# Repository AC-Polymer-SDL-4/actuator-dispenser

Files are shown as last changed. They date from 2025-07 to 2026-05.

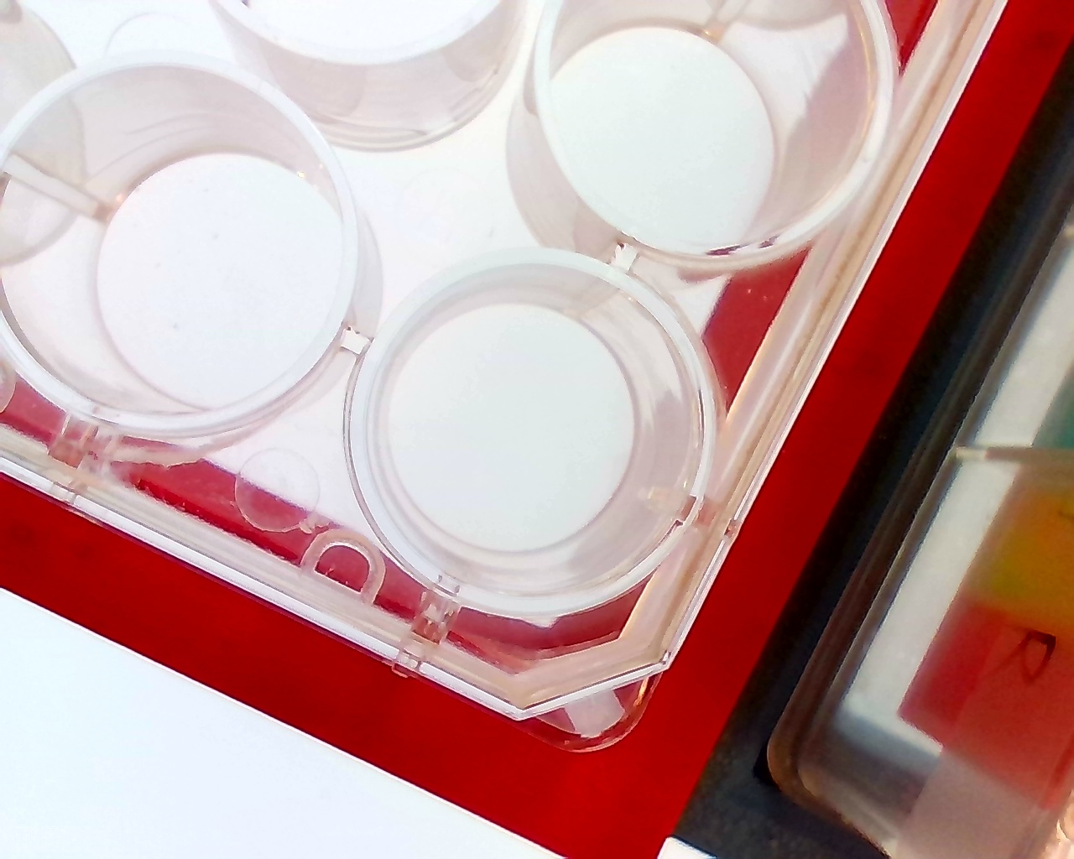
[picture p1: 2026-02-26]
captured_images/well_platewarmup_4.jpg

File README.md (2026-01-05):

# Ultra-budget liquid dispenser


## Overview
This repository contains an assembly guide, code, 3D-design files and data collected from using our ultra-budget liquid dispenser. With a small footprint, low cost (~$500 USD), short assembly time (4 hrs), full python integration and visual characterization, this system provides an accessible tool for developing self-driving (automated and AI-guided) workflows.

### Highlights of this system:
- Low cost (approx. $500 USD, see the [bill of materials](#bill-of-materials-bom) below)
- High customizability (3D-printed files can be adapted for different syringes / actuators / labware)
- Full python integration, with modular code design
- Short assembly time (approx. 4 hours)

### Folders included in this repo: 
1. `Hardware`: contains .f3d and .stl files for the 3D-printed labware holder, tool head and electronics casing, along with an assembly guide
2. `code`: contains the python files for the workflows, tests and code used to control the system and a user guide for code usage
3. `data`: contains the experimental data collected from color matching workflows (and PVA complexation workflows), referenced in the paper

### Authors:
Monique Ngan, David Okhimame, Harrison Mills, Owen Melville, Nipun Kumar Gupta <br>
[Acceleration Consortium](https://acceleration.utoronto.ca/) <br>
Last updated: Dec 8, 2025

## Summary of Assembly Guide
A complete assembly guide is provided in the `Hardware` folder.

### Bill of Materials (BoM)
All materials required to build this dispenser are listed below.
|Item|Manufacturer|Product Number|Qty|Cost ($USD)|Notes and Purpose|
|--|--|--|--|--|--|
|CNC Machine|Genmitsu|[3018-PROVer V2](https://www.amazon.com/Genmitsu-3018-PROVer-Beginner-Emergency-Stop-Spoilboard/dp/B0CMTJ6CZC/ref=sr_1_1_sspa?crid=114QL76VIJQT2&dib=eyJ2IjoiMSJ9.si54z4Io1GeuV5q_lf4cUYZaZCHezjGgIqHPUU6P0igZW3XxzJmYpZL9AtNIYYhJccTElgCcUhtUQdVV5ba8m4LS1GSoMPPCwf3UhyZvH4ZiUVoozKL17vWyOP9NJd20GuYpfVtuVC89muO9eLsUb9GWtYLfNeeW22jnDYMXf6Wj7DleAou0EVavEHKg_6sW3kLy3ayNA2Ds_glnvx3UoRy4-qHn3XDycz0rp29txVuko8hxuk06H_KGxhoJuUdYbvN3ssnQmkJF5SzANHrhnlooRnQT6lFYgSyDRnvIUy8.md_gFbjykxNHiYnS4wvrPfHJinOVtTMHGsAoOf21tVY&dib_tag=se&keywords=genmitsu+3018+pro&qid=1765214407&sprefix=%2Caps%2C61&sr=8-1-spons&sp_csd=d2lkZ2V0TmFtZT1zcF9hdGY&psc=1)|1|270.00|Gantry system|
|Backlight|HSK|[A4 Artist tracing Light Box](https://www.amazon.com/A4-Improved-Structure-Storage-Warranty/dp/B0755C2CBF/ref=sr_1_4_sspa?crid=HGMW73TTRQPR&dib=eyJ2IjoiMSJ9.4_N0Ik2-dp33AqZZQUH6lPCSK-indHZUztzxuA_r5m_N6FRgQakr2q2xWczA877ma-Kn3Wg1YssFvzX84_W71JBoGDrN-t-5l_fsytKcybtXcK0HeyLXEXp_SuL3Htm51K4VryE6UoOmJL38-CZoYn_D8gwmrOynzbvfrmPzWD8jF6ix13Yp7R2c_YWNEXzYW7PVZbbpmDKgD99cERhaPxwE0AcsIdEN1bAno8V0K94bn6aerwMUDKuRpkXaxoCaNUVZQ9D3wBQpVmUUeIcgyqLJ7cCkaRW__667lzrvsLQ.3viHBebDTzdf3RWMV6b_BhIbzKl7_wF7b8SZPi4-uwI&dib_tag=se&keywords=a4%2Bled%2Bpanel&qid=1765299952&sprefix=a4%2Bled%2Bpanel%2Caps%2C148&sr=8-4-spons&sp_csd=d2lkZ2V0TmFtZT1zcF9hdGY&th=1)|1|25.00|Enhances color visibility|
|Endoscope Camera|Tyenaza|[Endoscope Camera, Mobile Phone PC USB Type C](https://www.amazon.com/Endoscope-Camera-Mobile-Android-Automobile/dp/B0C6JR8TG8/ref=sr_1_10?dib=eyJ2IjoiMSJ9.UIx0_MnMRGRcN0FERPB60y0NFmOgdnMQwJY_1EN66x4e0-ot7XKPUeLJWaDTTIR6yV3tI7ThsW7LMkz1T1ZsGDWzj2Li6v4Vzr0u1RFGjRJIh_l7XIKk1Q0l5vpX20Y2uUF0HGad6THztKjjV1ANWd9QVDipdAZR5o26QjN-asDvbAYdY3iFJLmzDEKfAzMXOLw6BiDXPRqVsRnZXsVLfnMkuEQyuJAj5EdrKnWCnd5dk5_VgxRdt2Xlt7z77ri_MPU8DGG1KqCneqq29vXT1oAolqWyowlYc-aIQW_GiM8.EIXRIeel0Ufo-43jwhLEJ31pGBRFZajIRWRv7-a2gD0&dib_tag=se&keywords=endoscope+camera+pc&qid=1765299980&sr=8-10)|1|13.07|Visual Characterization|
|Actuator|Actuonix|[P8-25-165-12-P](https://www.robotshop.com/products/actuonix-p8-p-micro-linear-actuator-25mm-1651-12-volts)|1|101.00|Movement of syringe plunger|
|Microcontroller|Arduino|[UNO R4 Minima](https://www.digikey.com/en/products/detail/arduino/ABX00080/20371542?gclsrc=aw.ds&gad_source=1&gad_campaignid=23152963569&gbraid=0AAAAADrbLlh32xiJpBnvP6-kSLeiENSKG&gclid=Cj0KCQiAgP_JBhD-ARIsANpEMxzQU_KN7rieBYvX_7nYPHadNWN1wdzwr6caisf5aesis-2Pv4QOoUkaAu6rEALw_wcB)|1|20.00|Communication between computer and actuator|
|Motor Board|Arduino|[A000079](https://www.digikey.ca/en/products/detail/arduino/A000079/2784007)|1|28.4|Controls and powers actuator|
|12V Barrel Power Supply + Barrel Connector|ALITOVE|[12V DC Power Supply 2A](https://www.amazon.com/gp/aw/d/B07VQHCK6P/?th=1)|1|7.99|Microcontroller power supply|
|USB-C to USB-A Cable|DIYables|[DIY-USB-CABLE-UNO-R4](https://www.amazon.com/DIYables-Type-C-Cable-Arduino-Pieces/dp/B0CF575PW9/ref=sr_1_1?crid=1X5JRSBU5KXI3&dib=eyJ2IjoiMSJ9.xfdV7_O83Egk5hCZtzdxFgvndZUEhJk2wiER55T8da2XrHO9LYmdahZkSdnYATubZMWKmsgqLrut1veHztMaO_1m7VoN_dx0ihnui67jTtyK3FgLw7Rz-Eh6wyMHjEgAXv9i7K60oH5XuqyL5G4an2eJMNlM_DeC17x3jCVAVnJnZ6uyetzHWv7cU3cMDAj1BpTPr50KwHaxN_6sWH7-4z1DrrqwTndSrpDfoMHmvNGEaNXyxMRSGvqrmhN91ottXIMU9-Rr-A8sSM3ULrgUv6hOPjk3B-u5Lc4FVsLsT54.fcm_5GPGOIdKn36kKO_IwGwRgbkg4UXyGuoXdwWb4EE&dib_tag=se&keywords=USB%2BType-C%2BCable%2Bfor%2BArduino%2BUno%2BR4&qid=1765574974&s=electronics&sprefix=usb%2Btype-c%2Bcable%2Bfor%2Barduino%2Buno%2Br4%2Celectronics%2C101&sr=1-1&th=1)|1|7.99|For connection to microcontroller, comes in pack of 2|
|1 mL Glass Syringe|Bitomic|[1ML Borosilicate Glass Syringe with Silver Metal Plunger](https://www.amazon.com/Bitomic-Borosilicate-Anti-Leak-Accurate-Measuring/dp/B0B12N5FX1/ref=sr_1_4?crid=27Z7T6R5TKLKY&dib=eyJ2IjoiMSJ9.Yw4kuoOLBHtQtgRgCWrg_UyrphPhIigHygfRI9gIOsOOxc5vZB-vT6Ud9MmBn5jASPJFDirAoTOCDC5BUK4XhJrzwQ0H2fK1CxhK8O50jTiz1UXBEKUiPXQHhhY0z7NGUJ_H0zS58w3F-HV7qmqQ1KvSXZVnOcc-H95d0KyJQKOkdQ1ql96qCZtY4TWm8Ug5pwZGvPdHG9RO7FutGuSDnvlcll1teu8786hucaDxSbc.PAqqr5PJKCy80cdOngdv4AXuUCcV1T5XpCM-I6ynCME&dib_tag=se&keywords=1ml%2Bsyringe%2Bwith%2Bmetal%2Bplunger&qid=1761926550&sprefix=1ml%2Bsyringe%2Bwith%2Bmetal%2Bplunge%2Cspecialty-aps%2C86&sr=8-4-catcorr&srs=58792496011&th=1)|1|23.04|Comes in pack of 10 syringes|
|Blunt Syringe Needle|Knixxo|[Plastic Syringes Blunt Tip Needles](https://www.amazon.com/25-Pack-Plastic-Syringe-Syringes/dp/B0CNRLBPJX/?th=1)|1|10.16|Comes in pack of 25, we only use the 16Ga 1 Inch needle|
|3D-printed tool head and deck ware|n/a|n/a|1|5|Printed in PLA and PETG|
|3D-printed electronics box|n/a|n/a|1|2.18|Optional|
|Total Cost||||**approximately 500**||

### Other generic materials needed:
- Wires
- Screws (4 * M6-20mm, 1 * M3-25mm)
-	Nut (M3)
- Metal rod (2mm diameter, at least 80mm in length)
- Pliers
- Allen keys
- Super glue
- Access to a 3D printer, with PLA, PETG and 95A TPU filament

### Summary of steps for assembling this tool
_Total assembly time: approximately 4 hours_

1.	Order the required parts in the BoM.
2.	3D-print the files in the `Hardware/STL_Files` folder including the tool head, deckware holder, backlight clamps and optional electronics casing. If needed, editable models are provided in `Hardware/Fusion_Files`
3.	Assemble the CNC machine following the manufacturer's instructions (_2 hours_)
4.	Connect the actuator to the microcontroller and power supply (_20 mins_)
5.	Connect the device to your computer and code setup (_25+ mins, depending on your operating system_)
6.	Assemble the tool head (_50 mins_)
7.	Mount the backlight and deck ware holder (_optional, 5 mins_)

## Known issues
1. Gradual decrease in volume dispensed over time: It is recommended to **re-calibrate** the dispenser every 3 full 24-wellplates of experiments (~1200 liquid transfers) and **replace the syringe** every 6 well plates of experiments (~2000 liquid transfers).
2. The glass syringe may break over time due to repeated stress from the extension of the metal plunger: It is highly recommended to 3D-print the **TPU padding** (see the `Hardware/STL_Files` folder) and glue it to the bottom of the syringe plunger.

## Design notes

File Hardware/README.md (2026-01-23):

# Hardware Assembly Guide
## Summary of steps
_Total assembly time: approximately 4 hours_

1.	Order the required parts in the BoM.
2.	3D-print the files in the `Hardware/STL_Files` folder including the tool head, deckware holder, backlight clamps and optional electronics casing. If needed, editable models are provided in `Hardware/Fusion_Files`
3.	Assemble the CNC machine following the manufacturer's instructions (_2 hours_)
4.	Connect the actuator to the microcontroller and power supply (_20 mins_)
5.	Connect the device to your computer and code setup (_25+ mins, depending on your operating system_)
6.	Assemble the tool head (_50 mins_)
7.	Mount the backlight and deck ware holder (_optional, 5 mins_)
   
Please also read through the [**important notes**](#%EF%B8%8Fimportant-notes-things-to-watch-out-for-when-starting-workflows).

---
## Step 1: Order Required Parts
All materials required to build this dispenser are listed below:

### Bill of Materials (BoM)
|Item|Manufacturer|Product Number|Qty|Cost ($USD)|Notes and Purpose|
|--|--|--|--|--|--|
|CNC Machine|Genmitsu|[3018-PROVer V2](https://www.amazon.com/Genmitsu-3018-PROVer-Beginner-Emergency-Stop-Spoilboard/dp/B0CMTJ6CZC/ref=sr_1_1_sspa?crid=114QL76VIJQT2&dib=eyJ2IjoiMSJ9.si54z4Io1GeuV5q_lf4cUYZaZCHezjGgIqHPUU6P0igZW3XxzJmYpZL9AtNIYYhJccTElgCcUhtUQdVV5ba8m4LS1GSoMPPCwf3UhyZvH4ZiUVoozKL17vWyOP9NJd20GuYpfVtuVC89muO9eLsUb9GWtYLfNeeW22jnDYMXf6Wj7DleAou0EVavEHKg_6sW3kLy3ayNA2Ds_glnvx3UoRy4-qHn3XDycz0rp29txVuko8hxuk06H_KGxhoJuUdYbvN3ssnQmkJF5SzANHrhnlooRnQT6lFYgSyDRnvIUy8.md_gFbjykxNHiYnS4wvrPfHJinOVtTMHGsAoOf21tVY&dib_tag=se&keywords=genmitsu+3018+pro&qid=1765214407&sprefix=%2Caps%2C61&sr=8-1-spons&sp_csd=d2lkZ2V0TmFtZT1zcF9hdGY&psc=1)|1|270|Gantry system|
|Backlight|HSK|[A4 Artist tracing Light Box](https://www.amazon.com/A4-Improved-Structure-Storage-Warranty/dp/B0755C2CBF/ref=sr_1_4_sspa?crid=HGMW73TTRQPR&dib=eyJ2IjoiMSJ9.4_N0Ik2-dp33AqZZQUH6lPCSK-indHZUztzxuA_r5m_N6FRgQakr2q2xWczA877ma-Kn3Wg1YssFvzX84_W71JBoGDrN-t-5l_fsytKcybtXcK0HeyLXEXp_SuL3Htm51K4VryE6UoOmJL38-CZoYn_D8gwmrOynzbvfrmPzWD8jF6ix13Yp7R2c_YWNEXzYW7PVZbbpmDKgD99cERhaPxwE0AcsIdEN1bAno8V0K94bn6aerwMUDKuRpkXaxoCaNUVZQ9D3wBQpVmUUeIcgyqLJ7cCkaRW__667lzrvsLQ.3viHBebDTzdf3RWMV6b_BhIbzKl7_wF7b8SZPi4-uwI&dib_tag=se&keywords=a4%2Bled%2Bpanel&qid=1765299952&sprefix=a4%2Bled%2Bpanel%2Caps%2C148&sr=8-4-spons&sp_csd=d2lkZ2V0TmFtZT1zcF9hdGY&th=1)|1|25.00|Enhances color visibility|
|Endoscope Camera|Tyenaza|[Endoscope Camera, Mobile Phone PC USB Type C](https://www.amazon.com/Endoscope-Camera-Mobile-Android-Automobile/dp/B0C6JR8TG8/ref=sr_1_10?dib=eyJ2IjoiMSJ9.UIx0_MnMRGRcN0FERPB60y0NFmOgdnMQwJY_1EN66x4e0-ot7XKPUeLJWaDTTIR6yV3tI7ThsW7LMkz1T1ZsGDWzj2Li6v4Vzr0u1RFGjRJIh_l7XIKk1Q0l5vpX20Y2uUF0HGad6THztKjjV1ANWd9QVDipdAZR5o26QjN-asDvbAYdY3iFJLmzDEKfAzMXOLw6BiDXPRqVsRnZXsVLfnMkuEQyuJAj5EdrKnWCnd5dk5_VgxRdt2Xlt7z77ri_MPU8DGG1KqCneqq29vXT1oAolqWyowlYc-aIQW_GiM8.EIXRIeel0Ufo-43jwhLEJ31pGBRFZajIRWRv7-a2gD0&dib_tag=se&keywords=endoscope+camera+pc&qid=1765299980&sr=8-10)|1|13.07|Visual Characterization|
|Actuator|Actuonix|[P8-25-165-12-P](https://www.robotshop.com/products/actuonix-p8-p-micro-linear-actuator-25mm-1651-12-volts)|1|101|Movement of syringe plunger|
|1 mL Glass Syringe|Bitomic|[1ML Borosilicate Glass Syringe with Silver Metal Plunger](https://www.amazon.com/Bitomic-Borosilicate-Anti-Leak-Accurate-Measuring/dp/B0B12N5FX1/ref=sr_1_4?crid=27Z7T6R5TKLKY&dib=eyJ2IjoiMSJ9.Yw4kuoOLBHtQtgRgCWrg_UyrphPhIigHygfRI9gIOsOOxc5vZB-vT6Ud9MmBn5jASPJFDirAoTOCDC5BUK4XhJrzwQ0H2fK1CxhK8O50jTiz1UXBEKUiPXQHhhY0z7NGUJ_H0zS58w3F-HV7qmqQ1KvSXZVnOcc-H95d0KyJQKOkdQ1ql96qCZtY4TWm8Ug5pwZGvPdHG9RO7FutGuSDnvlcll1teu8786hucaDxSbc.PAqqr5PJKCy80cdOngdv4AXuUCcV1T5XpCM-I6ynCME&dib_tag=se&keywords=1ml%2Bsyringe%2Bwith%2Bmetal%2Bplunger&qid=1761926550&sprefix=1ml%2Bsyringe%2Bwith%2Bmetal%2Bplunge%2Cspecialty-aps%2C86&sr=8-4-catcorr&srs=58792496011&th=1)|1|23.04|Comes in pack of 10 syringes|
|Microcontroller|Arduino|[UNO R3](https://www.robotshop.com/products/arduino-uno-r3-usb-microcontroller)|1|30.08|Communication between computer and actuator|
|Motor Board|Arduino|[A000079](https://www.digikey.ca/en/products/detail/arduino/A000079/2784007)|1|28.4|Controls and powers actuator|
|12V Barrel Power Supply + Barrel Connector|ALITOVE|[12V DC Power Supply 2A](https://www.amazon.com/gp/aw/d/B07VQHCK6P/?th=1)|1|7.99|Microcontroller power supply|
|USB-C to USB-A Cable|DIYables|[DIY-USB-CABLE-UNO-R4](https://www.amazon.com/DIYables-Type-C-Cable-Arduino-Pieces/dp/B0CF575PW9/ref=sr_1_1?crid=1X5JRSBU5KXI3&dib=eyJ2IjoiMSJ9.xfdV7_O83Egk5hCZtzdxFgvndZUEhJk2wiER55T8da2XrHO9LYmdahZkSdnYATubZMWKmsgqLrut1veHztMaO_1m7VoN_dx0ihnui67jTtyK3FgLw7Rz-Eh6wyMHjEgAXv9i7K60oH5XuqyL5G4an2eJMNlM_DeC17x3jCVAVnJnZ6uyetzHWv7cU3cMDAj1BpTPr50KwHaxN_6sWH7-4z1DrrqwTndSrpDfoMHmvNGEaNXyxMRSGvqrmhN91ottXIMU9-Rr-A8sSM3ULrgUv6hOPjk3B-u5Lc4FVsLsT54.fcm_5GPGOIdKn36kKO_IwGwRgbkg4UXyGuoXdwWb4EE&dib_tag=se&keywords=USB%2BType-C%2BCable%2Bfor%2BArduino%2BUno%2BR4&qid=1765574974&s=electronics&sprefix=usb%2Btype-c%2Bcable%2Bfor%2Barduino%2Buno%2Br4%2Celectronics%2C101&sr=1-1&th=1)|1|7.99|For connection to microcontroller, comes in pack of 2|
|3D-printed tool head and deck ware|n/a|n/a|1|5|Printed in PLA and PETG|
|3D-printed electronics box|n/a|n/a|1|2.18|optional|
|Total Cost||||**514**||

### Generic Materials and Tools needed
- Wires
- Screws (4 * M6-20mm, 1 * M3-25mm)
-	Nut (M3)
- Metal rod (2mm diameter, at least 80mm in length)
- Pliers
- Allen keys
- Super glue
- Access to a 3D printer, with PLA, PETG and 95A TPU filament

## Step 2: 3D-print Required Parts
Please print the following .STL files with the filament and supports/settings listed. The editable Fusion 360 files for all these parts are provided in the `fusion files` folder, so this tool can be adapted to other types of labware, syringes, actuators or gantry systems.

|File|Purpose|Filament|Print instructions|
|--|--|--|--|
|Actuator_Holder_Plunger_Holder.stl|Holds together the syringe plunger and actuator|PETG|Print in the given orientation, with tree supports and 0.12mm layer height preset|
|Actuator_Holder_Tool_Head.stl|Holds parts together in CNC tool holder|PLA|Print in the given orientation, with tree supports and extra painted supports in the hanging circular ridges|
|Backlight_Clamp_Left.stl|Clamps backlight to CNC deck|PLA|Print with regular supports|
|Backlight_Clamp_Right.stl|Clamps backlight to CNC deck|PLA|Print with regular supports|
|Deckware_Holder.stl|Holds labware on CNC deck|PLA|Print with regular supports|
|Electronics_Box.stl|Optional, for organizing microcontroller and wires|PETG|n/a|
|Plunger_TPU_Cap.stl|Padding for metal syringe plunger|95A TPU|Print with 5mm outer brim, 0.1mm spacing|
|Reservoir_Spacer.stl|Raises reservoir to access bottom of wells|PLA|Print in the orientation provided, with normal supports|

## Step 3: Assemble the CNC machine 
The Genmitsu 3014 CNC machine comes with all the parts needed to build the CNC Machine and a manual with step-by-step instructions. We find that the Grblcontrol (Candle) app is a user-friendly way to control the CNC machine, when starting off, capturing the locations of the labware and for troubleshooting.

## Step 4: Connect Actuator to microcontroller and power supply
_Parts and materials required:_
-	Wires (red and black) + solder/jumper wires
-	Small screw for tightening connector terminals
-	Connector terminal with barrel opening
-	A metal rod with 2mm diameter

1. If using the optional electronics box, place the UNO R4 microcontroller at the bottom of the box, with the USB port aligned with the rectangular slot at the side of the box
2. Mount the motor shield above the microcontroller and ensure they are attached securely
3. To connect the power supply, insert a red wire into the positive (+) terminal and a black wire into the negative (-) terminal of the barrel connector. Tighten the screws and gently tug the wires to confirm they are secured. Then, connect the other end of the red wire to the VIN pin and the other end of the black wire to the GND pin on the motor shield. <br>


4. Wire the actuator: connect the red (positive) wire from the actuator to the A+ pin and the black (negative) wire from the actuator to A- on the motor shield. Use wire connectors or solder extensions if needed to ensure the wires are long enough for movement of the actuator in the CNC gantry.
5. Plug the 12V power supply into the barrel connector.
6. Connect the microcontroller to your computer using the USB-C / USB-A cable. There should be a green light in the microcontroller when connected.

## Step 5: Connect dispenser with computer and code set-up
1.	Install [Python version 3.10.11](https://www.python.org/downloads/release/python-31011/) and a code editor (e.g., [Visual Studio Code](https://code.visualstudio.com/Download)), if they aren’t already installed.
2.	Download the `code` folder, which includes all the code used to control the dispenser. More details on the code structure and customization can be found in the folder’s `README.md`.
3.	Plug in the USB cables for the CNC machine, microcontroller (actuator) and USB camera. On Windows, use the device manager app to find the COM PORT number of the CNC machine and microcontroller and determine the camera index (usually 0 or 1) of the USB camera. More details and debugging tips can be found in `code/README.md`.
4.	Install the packages listed in `code/requirements.txt`.
5.	Edit the COM PORT numbers in the code when initializing the dispenser or individual components to run tests and workflows.
	  -  For example: `dispenser = Liquid_Dispenser(cnc_comport="COM4", camera_index=0, acutuator_comport=”COM3”)` or `cnc = CNC_Machine(com = "COM4") `
7.	Run `tests/actuator_test.py` to check that the actuator is connected and working. This should retract and extend the plunger by ~0.5cm. If troubleshooting is needed, refer to `code/README.md`.

Additional details on the code design and functionality can be found in `code/README.md`.

## Step 6: Assemble Dispenser Tool Head
Tools and Materials needed:
-	Hex allen key
-	Pliers
-	1 Syringe + Needle
-	3D-Printed pieces: TPU padding, tool head and actuator_syringe_connector
-	Super-glue

1. Place the actuator into the top of the tool head, with the actuator shaft aligned with the square opening in the holder. After the actuator is inserted fully, thread the metal rod through the holder and top of the actuator. Then, check if the holes in the shaft are aligned with larger holes at the side of the holder. If not, use `actuator_test.py` to move the actuator up or down using the retract() and extend() methods respectively.
actuator_holder

2.	Glue the TPU padding to the bottom of the syringe plunger. After it dries, insert the plunger into the syringe.


3.	Attach the actuator syringe connector (shown in orange) to the top of the syringe plunger. The square at the top of the connector will be aligned with the actuator shaft in step 5.



4.	Place the syringe inside the tool holder (shown in blue).

 
5.	Align the square at the top of the orange connector piece with the actuator shaft (see image in step 3), then slowly push the plunger upwards until the holes in the connector are aligned with the holes in the actuator shaft. NOTE: check that the metal rod is still threaded in the top of the holder or else the actuator will be pushed up during this step.


6.	Insert the screw through the aligned holes and tighten the nut to secure the actuator to the plunger. 

 <br>
The following is how it should look when this step is complete: <br>


7.	Add the holder cap and insert the holder into the CNC tool holder. The circular part of the tool head should sit slightly below the top of CNC tool holder.


8.	Extend the plunger using `actuator_test.py` until the plunger is at the very bottom of the syringe. It is recommended to use intervals of 0.3 second extensions.
9.	Twist off the syringe cap and attach a new syringe needle by twisting it on.


10.	Place the camera into the slot in the front of the dispenser. If the hole was warped during the printing, use a heat gun to soften the print, insert the camera, and let it cool.


## Step 7: Deck set-up and mount labware 
1.	Place the backlight on the CNC deck. See below for a picture of the set-up.


2.	Using an Allen key, use 2 M6 screws to attach the left and right backlight clamps to the CNC deck. Position them near the recommended locations, as placing screws close to the edges of the X and Y axes may risk damaging the system when the gantry moves.
3.	If you are using the given labware set-up, place the well plate in the slot that is higher, and place a liquid reservoir inside the 3D printed reservoir spacer and into the other slot. If using other labware, feel free to adapt the deck ware holder and location coordinates in `code/location_status.yaml`.

_🎉Congratulations you have finished setting up the hardware for the ultra-budget liquid dispenser!_

## ⚠️IMPORTANT NOTES: Things to watch out for when starting workflows
1. Ensure the metal rod at the top of the holder is in place; it keeps the actuator secured when moving
    <br>

2. Ensure the camera is securely placed in the front of the tool head
   - Test its positionings using `cnc_camera_test.py` to make sure you don’t pick up the edges of the wells
   - Edit location_status.yaml, decrease the crop size or adjust the camera if needed
   - 
     
3.	Ensure the actuator is fully extended & plunger is at the bottom of the syringe. Since the position of the syringe is not tracked, pulling it too far up can break the dispenser.
     - If not, use `code\test\actuator_test.py` to move the plunger

4.	It is recommended to **re-calibrate** the dispenser every 3 full 24-wellplates of experiments (**~1200** liquid transfers) and switch to a **new syringe** every 6 well plates of experiments (**~2000** liquid transfers).
     - For calibrations, run `volume_calibration.py` to calibrate the system for accurate liquid transfer

## Replacing the syringe
_Tools and Materials needed:_
-	Hex allen key
-	Pliers
-	New syringe
-	New syringe needle (optional)

1.	Remove tool head from the CNC holder and remove the cap.
2.	Move the syringe up so the screw and nut are aligned with the holes at the side of the holder using `act.retract()` or `act.extend()` in `actuator_test.py`. It is recommended to use time intervals of 0.3 seconds. 
3.	Hold the screw in place using an Allen key and use pliers to unfasten the nut. Then, remove the screw.
    

4.	Remove the orange connector pieces to release the old syringe from the actuator.
5.	To install the new syringe, follow the same steps in [step 6](#step-6-assemble-dispenser-tool-head) of this assembly guide.

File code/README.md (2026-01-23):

# Code set-up & User Guide

## Basic installation instructions:
1. Install [Python version 3.10.11](https://www.python.org/downloads/release/python-31011/) and a code editor (e.g., [Visual Studio Code](https://code.visualstudio.com/Download)), if they aren’t already installed.
2.	Download the `code` folder, which includes all the code used to control the dispenser. Below are more details about the code structure, workflows and tests to run when setting up the dispenser.
3.	Plug in the USB cables for the CNC machine, microcontroller (actuator) and USB camera. On Windows, use the device manager app to find the COM PORT number of the CNC machine and microcontroller and determine the camera index (usually 0 or 1) of the USB camera.
4.	Create a virtual environment for this project and install the python packages listed in `code/requirements.txt`.
5.	Edit the COM PORT numbers in the code when initializing the dispenser or individual components to run tests and workflows.
	  -  For example: `dispenser = Liquid_Dispenser(cnc_comport="COM4", camera_index=0, acutuator_comport="COM3")` or `cnc = CNC_Machine(com = "COM4")`

## Code Structure
The code is set up in a modular way, where there are separate classes controlling each of the components (e.g., the camera, actuator and CNC machine) and a high-level dispenser class that orchestrates all these components. This structure makes it easier to add or switch the components in the dispenser (e.g., adding a pH probe to the tool head) and to reuse the code written for the existing components (like the CNC machine class for another CNC-based tool).

Here are highlighted functions within each of the classes:
|Component|Class Name|Key Functions|
|--|--|--|
|Camera|Camera|<ul><li>`capture_and_save()`: captures images using the camera and returns the file path</li> <li>`average_color_in_center()`: analyze images to determine color space coordinates</li></ul>|
|Actuator|ActuatorRemote| <ul><li>`retract()`: retract actuator to withdraw liquid</li><li>`extend()`: extend actuator to dispense liquid </li> </ul>|
|CNC Machine|CNC_Machine|<ul><li>`move_to_location()`: move tool head to a location saved in `locations_status.yaml`</li></ul>|
|Dispenser|Liquid_Dispenser|<ul><li>`dispense_between()`: transfer liquid from a source location to a destination location, with different liquid transfer parameters like syringe speed, buffer volume <ul> <li>Incorportates CNC movements to the locations and the actuator for liquid manipulation </li></ul></li> <li>`get_image_color()`: moves camera to the designated well to capture and analyze the images for color coordinates <ul><li>Incorportates CNC movements to the locations and the camera for image capture and analysis </li></ul> </li> </ul>|

## Example workflows
Some example workflows included are: 
1.	`color_matching_workflow.py`: A self-driving workflow using Bayesian Optimization (BO) to match an unknown target color from red, blue and yellow solutions using visual feedback.
    - This workflow contains all the code for the physical actions and calls from `color_matching_optimizer.py` for BO tasks like initializing the BayBE campaign and getting new suggestions.
    - The data and images collected are in `data\color_matching`
    - Deck set-up: a reservoir with color solutions and water for rinsing the syringe and a 24-wellplate with 1mL of the unknown target color (a combination of the color solutions) in the top-left well in the wellplate. See image below.
    - 

## Troubleshooting connection issues
1.	Make sure all components are plugged in (microcontroller, CNC machine (with the power switch on), optionally the backlight) and connected to the computer via USB (microcontroller, camera, CNC machine)
2.	Isolate which component isn’t working by running the test files:
	- Edit the `com_port` value for the CNC machine and run `cnc_machine_test.py`, this should home the cnc machine.
		- If there are permission_denied errors: make sure Candle is NOT open, and double check the comport number in device manager
	- Edit the `camera_index` value (usually 0 or 1) and run `Camera_test.py`, this should capture an image and save it to the designated output folder.
 		- If there are initialization errors: change the camera_index, and check that you can access the camera using a camera app on your computer
	- Edit the `com_port` value in `actuator_test.py` and run, this should retract and extend the actuator by ~0.5cm. There is also a sound when the actuator is moving.
		- If the actuator doesn’t move:
			- check the microcontroller to see if it is connected to your computer (green light) 
			- run the test again and check if there are orange lights at the A+ and A- pins on the motor board when sending each of the commands
				- if yes, the motor shield is powered but power is not reaching the actuator ==> check the wiring to the actuator and make sure everything is connected
				- if none, this means the motor shield is not powered ==> check the power supply to the actuator
    	- If all of these did not diagnose the issue: use a multimeter in voltage mode to confirm whether power (12V) is supplied throughout the system

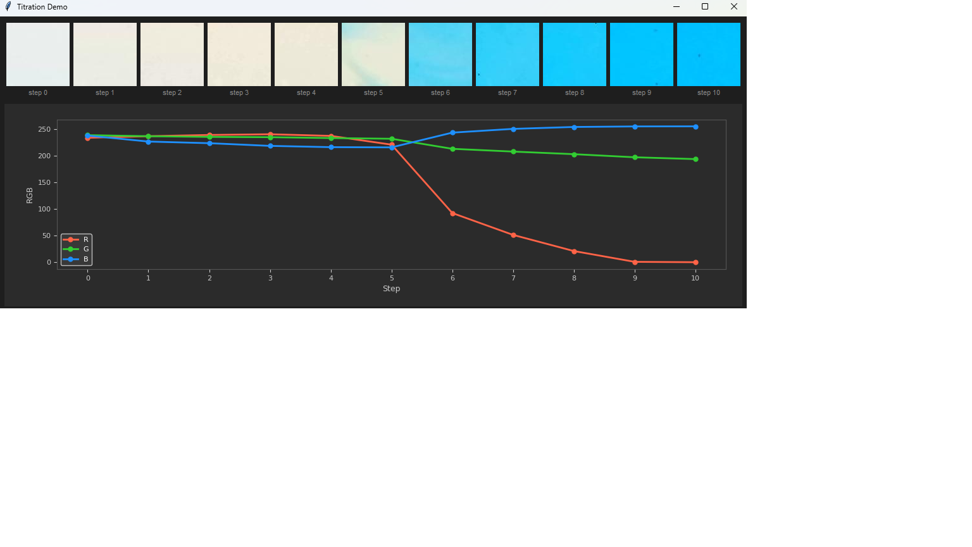
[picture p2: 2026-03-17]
titration.png

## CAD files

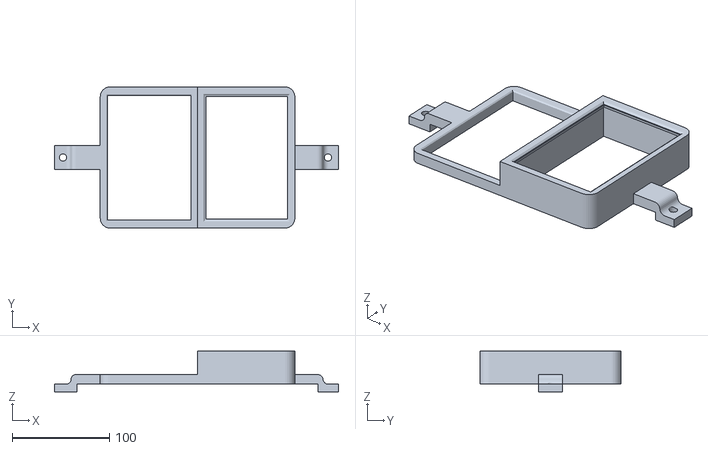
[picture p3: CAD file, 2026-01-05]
Hardware/STL Files/Deckware_Holder.stl
291.8 x 145.0 x 41.8

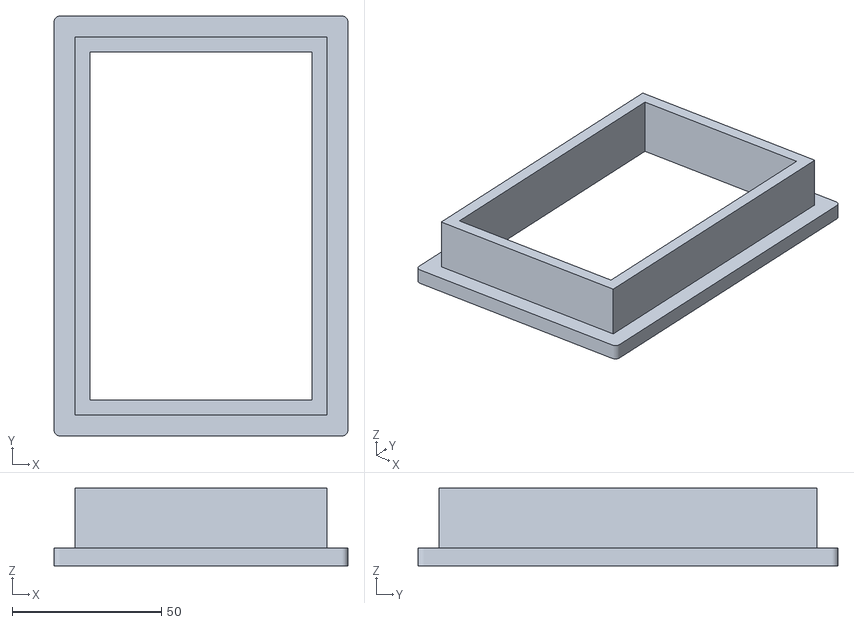
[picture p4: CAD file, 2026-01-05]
Hardware/STL Files/Reservoir_Spacer.stl
98.5 x 140.8 x 26.0

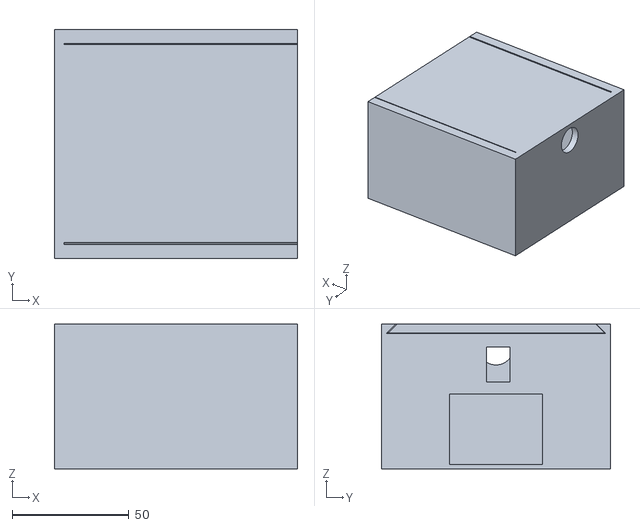
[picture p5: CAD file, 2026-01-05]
Hardware/STL Files/Electronics_Box.stl
104.0 x 98.0 x 62.0

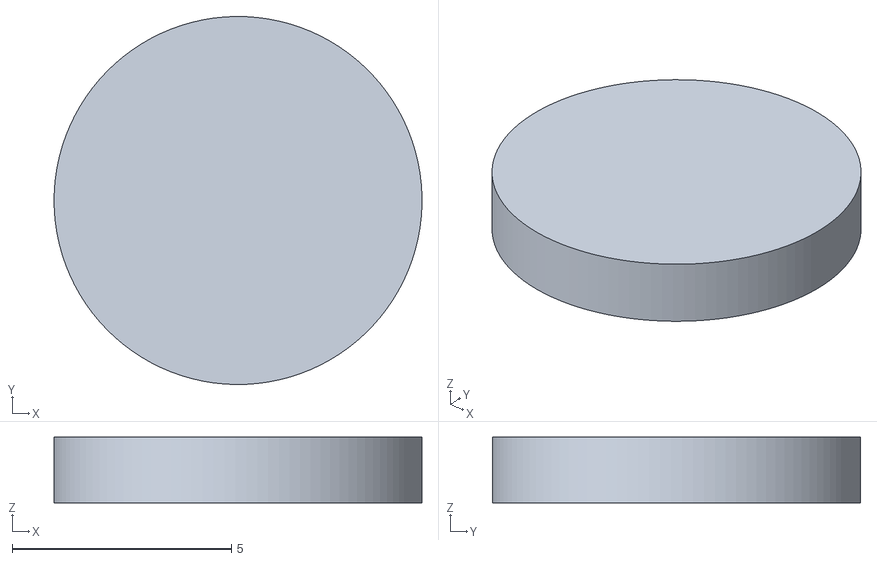
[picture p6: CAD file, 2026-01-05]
Hardware/STL Files/Plunger_TPU_Cap.stl
8.40 x 8.40 x 1.50

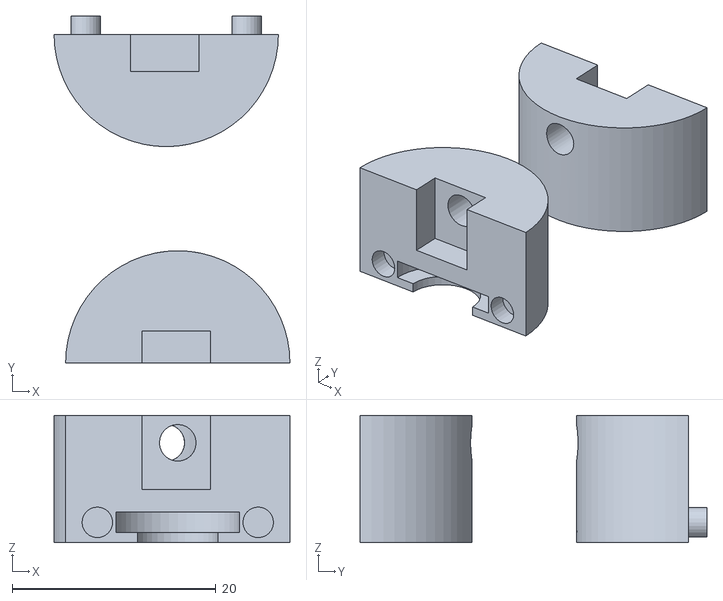
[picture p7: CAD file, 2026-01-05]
Hardware/STL Files/Actuator_Holder_Plunger_Holder.stl
23.1 x 34.0 x 12.5

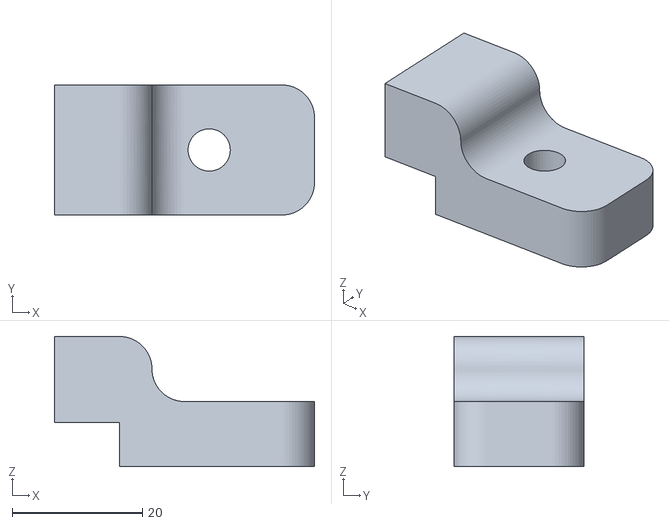
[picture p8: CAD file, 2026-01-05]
Hardware/STL Files/Backlight_Clamp_Right.stl
40.0 x 20.0 x 20.0

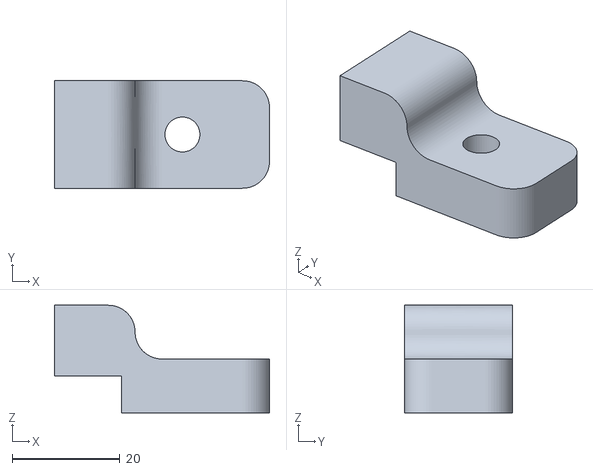
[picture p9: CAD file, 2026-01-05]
Hardware/STL Files/Backlight_Clamp_Left.stl
40.0 x 20.0 x 20.0

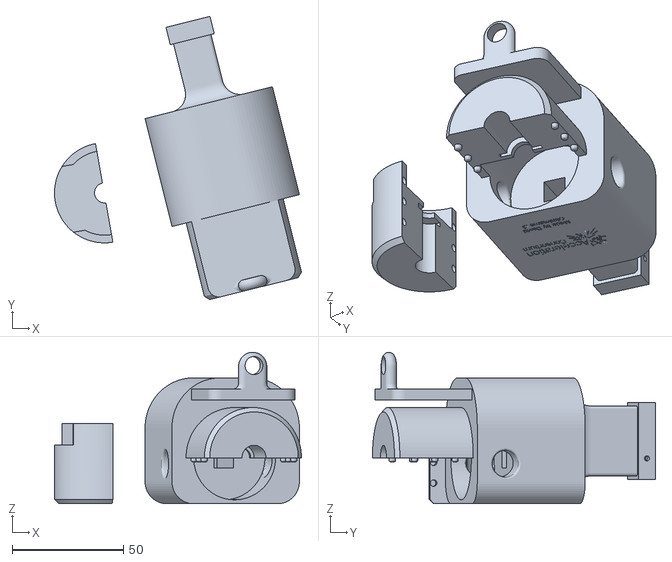
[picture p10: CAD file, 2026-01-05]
Hardware/STL Files/Actuator_Holder_Tool_Head.stl
111.0 x 127.3 x 68.1

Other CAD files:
Hardware/Fusion Files/Actuator_Holder.f3d
Hardware/Fusion Files/Backlight_Clamp_Left.f3d
Hardware/Fusion Files/Backlight_Clamp_Right.f3d
Hardware/Fusion Files/Electronics_Box.f3d
Hardware/Fusion Files/Plunger_TPU_Cap.f3d
Hardware/Fusion Files/Reservoir_Spacer.f3d

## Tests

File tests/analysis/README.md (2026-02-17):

# Analysis Scripts

This folder contains the streamlined analysis tools for uncertainty workflow outputs.

- `uncertainty_plot_and_stats.py`: Primary analysis and plotting script. Generates trends, normalized channels (`R'`, `G'`, `B'`, LAB, HSV), dotted expected overlays (water-scaled `R*0.9`, `Y*0.9`, `B*0.9`), group stats, and ANOVA.
- `validate_normalized.py`: Sanity checks for `normalized_channels.csv` (ranges, sum-to-one where applicable).
- `concentration_calibration.py`: Fits a simple mixing model from normalized RGB to dye fractions; predicts fractions per well and outputs calibration plots.

Notes:
- Expected compositions are centralized in `uncertainty_plot_and_stats.get_expected_compositions()`.
- RGB normalization uses sRGB gamma decode to linear-light before computing fractions.

## Camera sRGB Check
Use `camera_srgb_check.py` to verify the camera delivers 8‑bit, 3‑channel frames and to estimate whether frames are sRGB‑like gamma coded.

Example:

```bash
python tests/analysis/camera_srgb_check.py --device 0 --backend dshow --width 1280 --height 720
```

What it does:
- Captures a frame, checks `uint8` dtype and 3‑channel shape.
- Records capture properties (width/height/fps/FourCC/convert_rgb).
- Saves a sample PNG and a text report under `output/cnc_camera_test/<timestamp>/camera_srgb_check/`.
- Compares luminance under linear vs sRGB decode vs pure gamma=2.2; a ratio (MSE_gamma22/MSE_linear) < 0.6 suggests sRGB‑like gamma behavior.

Notes:
- On Windows, `--backend dshow` typically yields stable capture of BGR8 frames.
- If you want to also save the raw numpy array, add `--save-npy`.

Deprecated helpers were removed to reduce redundancy. Use the main script and validators above for routine analysis.

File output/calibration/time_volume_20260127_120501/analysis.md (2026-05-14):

# Time → Net Mass Calibration Analysis

**Dataset:** output/calibration/time_volume_20260127_120501/calibration_measurements_net.csv

## Fit Summary
- k (g/s): 0.3811
- b (g): 0.0041
- R^2: 0.9877
- RMSE (g): 0.0161
- Seconds per gram (s/g): 2.6238
- N (rows): 48

## Per-Time Statistics (replicate variability)
Columns: time_s, N, mean_g, sd_g, cv_%, se_g, ci95_g

| time_s | N | mean_g | sd_g | cv_% | se_g | ci95_g |
| --- | --- | --- | --- | --- | --- | --- |
| 0.05 | 4.0 | 0.024 | 0.0012 | 4.81 | 0.0006 | 0.0011 |
| 0.16 | 4.0 | 0.0658 | 0.0067 | 10.12 | 0.0033 | 0.0065 |
| 0.27 | 4.0 | 0.1085 | 0.0029 | 2.66 | 0.0014 | 0.0028 |
| 0.38 | 4.0 | 0.148 | 0.0032 | 2.14 | 0.0016 | 0.0031 |
| 0.49 | 4.0 | 0.1868 | 0.0334 | 17.9 | 0.0167 | 0.0328 |
| 0.6 | 4.0 | 0.2258 | 0.0115 | 5.11 | 0.0058 | 0.0113 |
| 0.71 | 4.0 | 0.2802 | 0.0153 | 5.45 | 0.0076 | 0.015 |
| 0.82 | 4.0 | 0.317 | 0.015 | 4.73 | 0.0075 | 0.0147 |
| 0.93 | 4.0 | 0.3622 | 0.0247 | 6.82 | 0.0124 | 0.0242 |
| 1.04 | 4.0 | 0.4028 | 0.0211 | 5.24 | 0.0106 | 0.0207 |
| 1.15 | 4.0 | 0.4468 | 0.0157 | 3.52 | 0.0079 | 0.0154 |
| 1.25 | 4.0 | 0.4732 | 0.0286 | 6.04 | 0.0143 | 0.028 |

## Observations
- Strong linearity with high R^2; small intercept.
- Typical single-dispense SD ~0.015 g (median) and CV ~5%.
- Absolute SD increases with time (heteroscedasticity); relative CV generally mid-single digits.
- Some timings show elevated variability (e.g., spikes visible in table).

## Artifacts
- Plot: output/calibration/time_volume_20260127_120501/time_to_net_mass_fit.png
- Fit summary: output/calibration/time_volume_20260127_120501/time_net_mass_fit_summary.txt
- Per-time stats CSV: output/calibration/time_volume_20260127_120501/per_time_stats.csv

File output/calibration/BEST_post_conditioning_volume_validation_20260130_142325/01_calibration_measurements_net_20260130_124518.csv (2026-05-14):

calibration_type | volume_index | plate_index | replicate | well_index | target_volume_ml | dispensed_mass_g | dispensed_volume_ml | measured_mass_g | baseline_mass_g | air_time_s | retract_time_s | extend_time_s | buffer_time_s | blowout_vol_ml | speed | timestamp
volume_dispenser | 0 | 0 | 1 | 0 | 0.2 | 0.206 | 0.206 | 43.818 | 43.612 |  |  |  | 0.25 | 0.2843 | 32768 | 2026-01-30 12:46:42
volume_dispenser | 0 | 0 | 2 | 1 | 0.2 | 0.192 | 0.192 | 44.01 | 43.818 |  |  |  | 0.25 | 0.2843 | 32768 | 2026-01-30 12:47:48

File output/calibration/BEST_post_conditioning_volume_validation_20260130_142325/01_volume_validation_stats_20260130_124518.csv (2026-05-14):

target_volume_mL | mean | std | count | cv_percent
0.2 | 0.19899999999999807 | 0.009899494936608692 | 2 | 4.9746205711601945

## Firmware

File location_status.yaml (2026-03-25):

vial_rack: #Array-location
  num_x: 2 #Columns
  num_y: 4 #Rows
  x_origin: 79.000 #move the cnc machine with the needle attached, and find the position 
  y_origin: 99.000
  z_origin: 0
  x_offset: 37 #Measure with caliper
  y_offset: -32 #MEasure with caliper
  aspirate_height: none
  dispense_height: 0
  mixing_height: none
vial_rack_12: #Array-location
  num_x: 3 #Columns
  num_y: 4 #Rows
  x_origin: 125 #move the cnc machine with the needle attached, and find the position 
  y_origin: 93.5
  z_origin: 0
  x_offset: -28.5 #Measure with caliper
  y_offset: -29 #MEasure with caliper
  aspirate_height: -70
  dispense_height: -15
  mixing_height: -70
reservoir_12: #Array-location
  num_x: 1 #Rows
  num_y: 12 #Columns
  x_origin: 97.0 #move the cnc machine with the needle attached, and find the position 
  y_origin: 100.5
  z_origin: 0 #-64 (inside dispense_between()) 
  x_offset: 0 #Measure with caliper
  y_offset: -8.92 #MEasure with caliper
  aspirate_height: -70
  dispense_height: -15
  mixing_height: -70
well_plate: #Array-location
  num_x: 4 #Rows
  num_y: 6 #Columns
  x_origin: 168.000 #move the cnc machine with the needle attached, and find the position 
  y_origin: 101.000
  z_origin: 0
  x_offset: 19 #Measure with caliper
  y_offset: -19.5 #MEasure with caliper
  aspirate_height: none
  dispense_height: -25
  mixing_height: -58
well_plate_camera: #Array-location
  num_x: 4 #Rows
  num_y: 6 #Columns
  x_origin: 172.000 #move the cnc machine with the needle attached, and find the position , 168 before
  y_origin: 143.000 #137 before
  z_origin: -10
  x_offset: 20 #Measure with caliper (20)
  y_offset: -19.2 #MEasure with caliper -18.9
  aspirate_height: none
  dispense_height: none
  mixing_height: none

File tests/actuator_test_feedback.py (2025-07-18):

from machine import Pin, ADC, PWM
import time

IN1 = Pin(26, Pin.OUT)
IN2 = Pin(25, Pin.OUT)
ENA = PWM(Pin(27))
ENA.freq(1000)

adc = ADC(Pin(34))
adc.atten(ADC.ATTN_11DB)
adc.width(ADC.WIDTH_12BIT)

def extend():
    IN1.value(1)
    IN2.value(0)
    ENA.duty(512)

def retract():
    IN1.value(0)
    IN2.value(1)
    ENA.duty(512)

def stop_motor():
    ENA.duty(0)
    IN1.value(0)
    IN2.value(0)

def read_position():
    return adc.read()

print("Extending for 5 seconds...")
extend()
start = time.ticks_ms()
while time.ticks_diff(time.ticks_ms(), start) < 5000:
    position = read_position()
    print("Position:", position)
    time.sleep(0.1)
    if position < 300:
        stop_motor()

# stop_motor()

# print("Waiting 1 second before retracting...")
# time.sleep(1)

# print("Retracting for 5 seconds...")
# retract()
# start = time.ticks_ms()
# while time.ticks_diff(time.ticks_ms(), start) < 5000:
#     print("Position:", read_position())
#     time.sleep(0.1)
# stop_motor()

print("Done.")

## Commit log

2025-08-08 Final code
    fixed bugs
    [well_plate_data.csv]
2025-08-29 Finished Code
    [Acuator Holder NEW (8,07).f3d, backlight_clamp.f3d, backlight_clamp_Left.f3d]
2025-09-26 testing reservoir and camera
2025-10-17 Refactor color matching workflow and update dispenser functionality
    [color_matching_results_20250925_161547.csv, color_matching_results_20250925_163110.csv, color_matching_results_20250925_163258.csv, color_matching_results_2025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]
2025-11-11 Updated dispensing for new metal syringe plunger, added real time saving of image color results
2025-12-10 Create assembly guide README.md
2025-12-18 Update calibration parameters, adjust COM ports, and clean up test scripts
2025-12-22 Update dispenser calibration values and clean up test scripts
2025-12-23 Update README.md
    Updated microcontroller reference and revised materials list.
2025-12-29 Uploaded 3D models
    [Actuator_Holder.f3d, Actuator_Holder_Plunger_Holder.stl, Actuator_Holder_Tool_Head.stl, Backlight_Clamp_Left.f3d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]
2025-12-29 updated 3d files
    [Deckware_Holder.stl]
2025-12-29 Update 3D-printing instructions and add new files
2025-12-31 Update README.md
    Updated assembly instructions and Bill of Materials for clarity and accuracy.
2026-01-05 Update README.md
    Updated instructions for actuator installation and added notes for camera placement and backlight setup.
2026-01-29 calibration first take
2026-01-29 Add compute_net_mass script and update calibration constants and volume calibration logic
2026-01-29 Refactor calibration scripts and add camera capture functionality
    - Updated `compute_net_mass.py` to improve mass calculation logic and added support for direct dispensed mass.
    - Modified `constants.py` to adjust MAX_TIME_S for actuator operations.
    - Introduced new test scripts `focused_time_retest.py` and `focused_time_retest_2.py` for time-based volume calibration.
    - Enhanced `time_net_mass_analysis.py` to compute and save per-time statistics.
    - Simplified `volume_calibration.py` by fixing calibration times and streamlining the dispensing process.
    - Added `camera_capture_only.py` for capturing images without CNC operations.
    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
2026-01-29 Enhance calibration scripts: update sys.path for imports and add argument parsing for CSV input in time_net_mass_analysis
2026-01-29 Add volume validation scripts and update dispenser logic for improved calibration accuracy
2026-02-06 Enhance camera functionality: add anti-flicker exposure tuning, improve camera initialization with backend fallbacks, and implement pre-wet and tip conditioning options in volume validation tests.
2026-02-13 analysis: add normalization scripts and plots; camera fallback reopen + preflight; CNC Z bound update; tests and camera checks
2026-02-13 data: add selected uncertainty run outputs (20260213_073533) for sharing
    [expected_rgb_error.csv, measurement_summary.csv, measurements_progress_group_1.csv, measurements_progress_group_2.csv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]
2026-02-13 data: add all uncertainty_measurement_workflow outputs to repo
    [expected_rgb_error.csv, measurement_summary.csv, measurements_progress_group_1.csv, measurements_progress_group_2.csv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]
2026-02-17 plots: add generated graphs and stats for 20260213 darkest green runs
    [expected_rgb_error.csv, measurement_summary.csv, measurements_progress_group_1.csv, measurements_progress_group_2.csv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]
2026-02-17 plots: use raw expected fractions for dotted lines; regenerate 20260213_073533 outputs
    [expected_rgb_error.csv, measurement_summary.csv, measurements_progress_group_1.csv, measurements_progress_group_2.csv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]
2026-02-17 plots: use water-scaled expected overlays (dye*0.9) across all normalized RGB plots; keep error as dye-normalized
    [expected_rgb_error.csv]
2026-02-17 analysis cleanup: stub camera_srgb_check.py, centralize expected comps, add README; deprecate redundant helpers
2026-02-17 Fix color normalization: remove incorrect sum-normalized variants for LAB/HSV, update filenames to normalized.png, delete old incorrect graphs
    [normalized_channels.csv]
2026-05-14 Add all output folder contents
    [20260220_130448_automated_darkest_more_yellow_7_1_1_sensitivity.csv, 20260220_152241_automated_darkest_more_yellow_7_1_1_sensitivity.csv, aggregate_combined_st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]
2026-05-31 Curate paper-ready analysis datasets
    [01_calibration_measurements_net_20260130_124518.csv, 01_volume_validation_stats_20260130_124518.csv, 02_calibration_measurements_net_20260130_140415.csv, 02_vo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]
2026-06-12 Refactor code structure for improved readability and maintainability
    [measurement_vs_process_uncertainty_by_group_channel.csv, measurement_vs_process_uncertainty_summary.csv, sensitivity_coefficients_with_response_strength.csv, u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]
